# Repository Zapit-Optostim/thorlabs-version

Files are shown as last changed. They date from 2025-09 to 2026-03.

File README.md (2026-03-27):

# zapit-CAD

Zapit is a random-access spatio-temporally precise scanning system for optogenetics experiments. This repo consists of resources on the parts used, CAD models for their construction and instructions for assembly. 

See the [Parts List](Parts_List.md) for a list of parts required for constructing Zapit.

The CAD models show you each part needed (where available) to construct the system and a rendering of how these pieces should be put together. 

The orientation of the parts are not set in stone, and therefore do not have to be set exactly as they are in these models. However,  the 'order' of pieces is very important, and it helps to think about this best in terms of the direction of the light path from the laser (see Fig. 1a in the paper to help with visualisation). Additionally, the distance between parts is dependent on the objective and tube lenses you use for the distance needed from your sample. Please get in touch if you have trouble finding the right combination for your experiments. 

We also have adaptor parts for each laser in the 'Thorlabs-parts' folder to connect the laser to Thorlabs parts, which are the only custom part as part of this system design. These parts have worked for us but you are free to design and machine your own. We recommend getting these adaptor plates CNC milled, rather than 3D printed, as depending on your stimulation protocol, these lasers are prone to overheating, which may turn your laser off automatically within an experiment (such as with the Obis lasers). These parts are also only appropriate if you are using the laser without their corresponding heatsink. If you are using the heatsink, you will have to design your own part to attach both the laser and heatsink. 

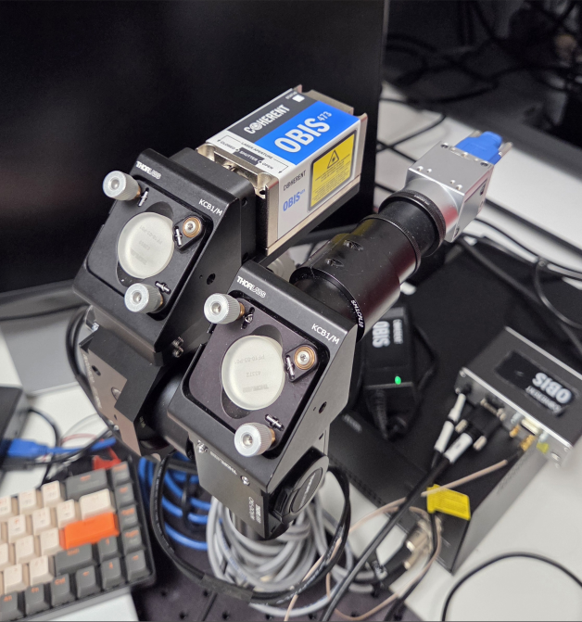
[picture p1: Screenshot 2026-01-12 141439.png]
 

We are keen to help others build the system, so if you feel you lack information please make contact via GitHub and we will get you up and running. 

If you need additional sound-proofing, you can build the custom enclosure, which is found [here](https://github.com/Zapit-Optostim/zapit_CAD)

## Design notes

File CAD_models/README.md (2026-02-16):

The following is a set of assembly instructions for the Thorlabs set up. This is the same for all lasers, the only changes are the laser, adaptor plate and filters needed.

If you want to change the focal distances based on your set up (which depends on how far the mouse is from the lens), the larger of the focal distance lens combinations (see paper, under Hardware design) should be the objective lens to keep the magnification at 0.5x.
You can also change the length of the rods for your needs, and how close you want pieces coupled together.

| Step | Instruction | Visual Aid |
| ---- | ----------- | ---------- |
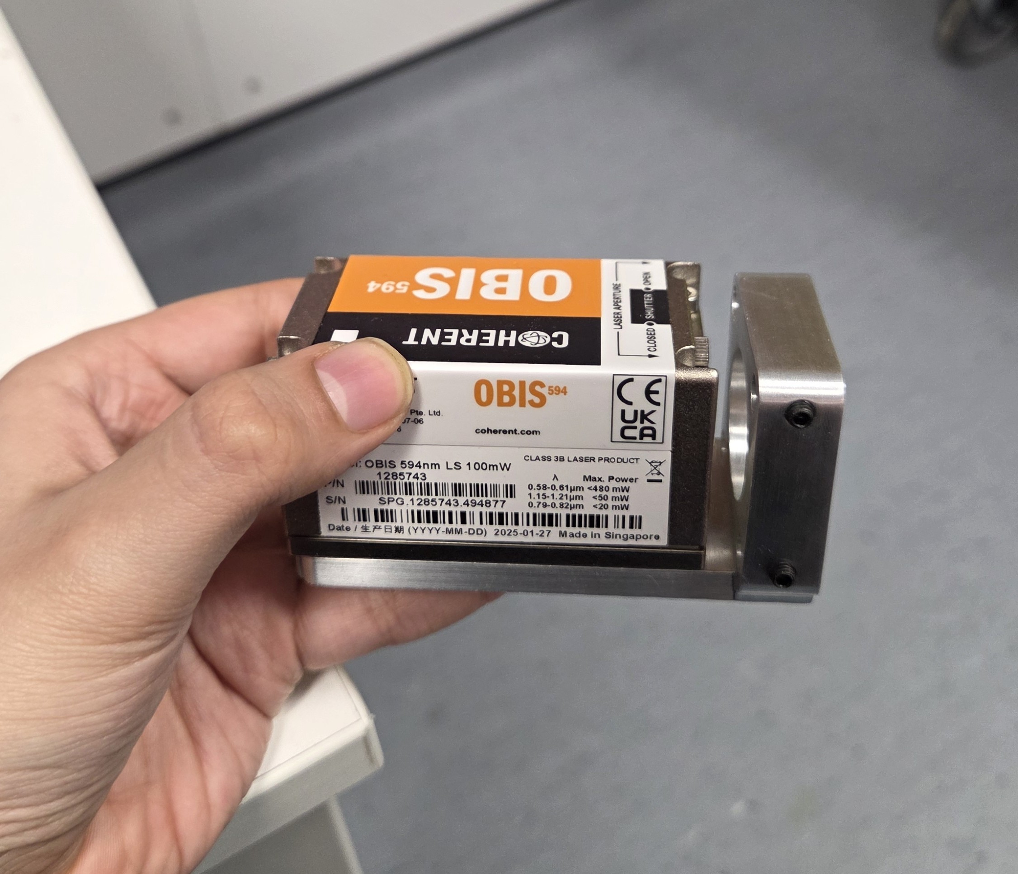
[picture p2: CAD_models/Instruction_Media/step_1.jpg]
Step 1
|   1  | Attach the laser to the adaptor plate with screws (check the hole size in CAD).| |
|  2   | Carefully place a silver mirror (PFR10-03-P01) in a right angled mirror holder (KC1B/M) by loosening the black side screw to make room for the silver mirror insertion (reflective side facing inwards), and then tighten to lock it into place.| Step 2|
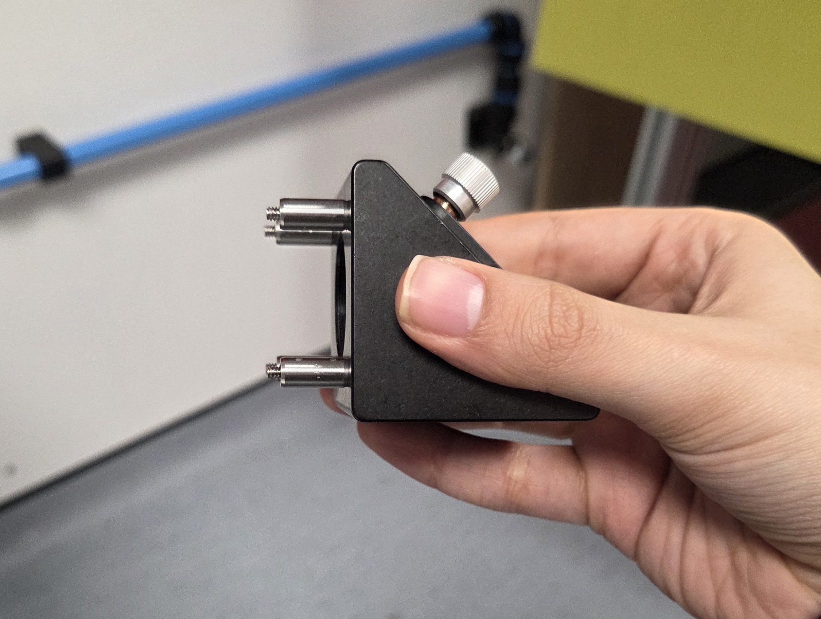
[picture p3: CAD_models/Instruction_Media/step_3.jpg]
Step 3
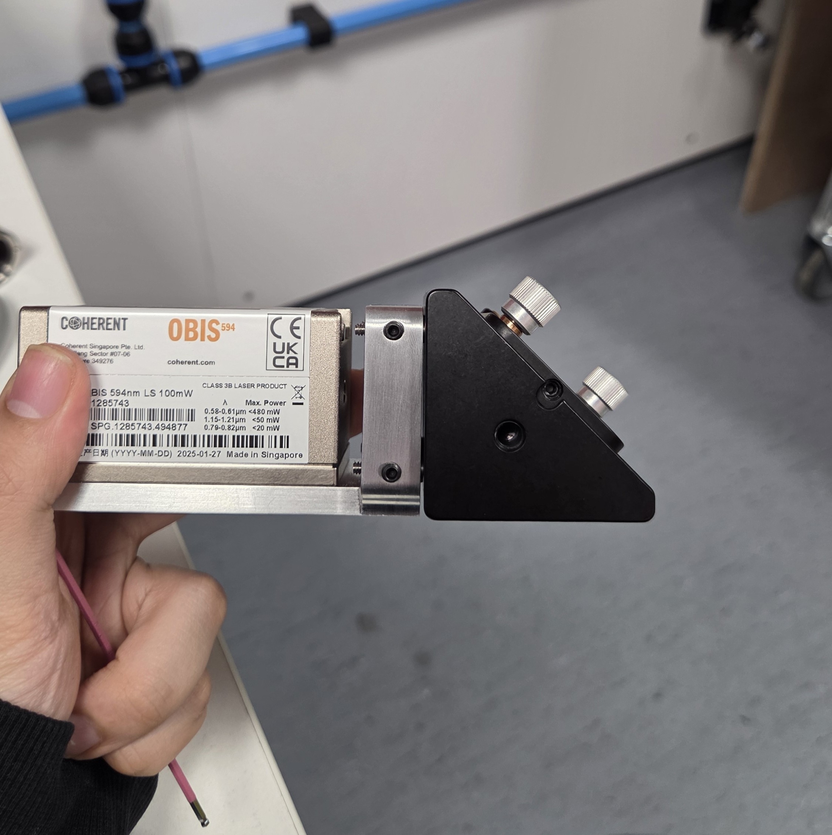
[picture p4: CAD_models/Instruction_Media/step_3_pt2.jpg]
Step 3 Continued
|  3   | Screw in cage rods (ER05) into the same KC1B/M part above in order to connect the laser adapter plate to the right angled mirror holder. Check the side holes in the CAD model to see which size screws you need for securing the ER rods into the custom adaptor plate.|  |
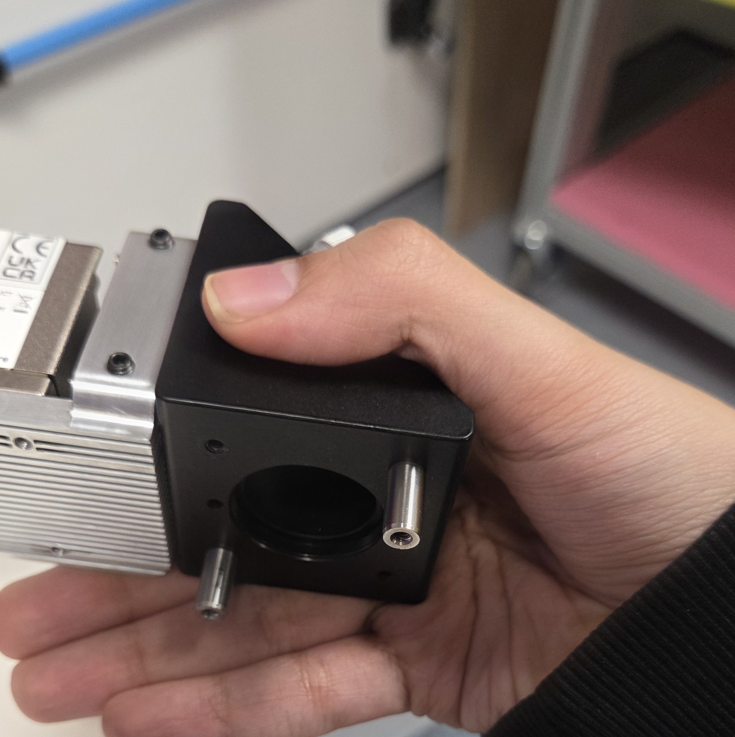
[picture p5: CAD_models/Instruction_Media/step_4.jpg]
Step 4
|  4   | Screw in ER05 rods into the other side of the KC1B/M part.| |
|  5   | Attach a lens tube (SM1L03) to couplers (SM1T010) on one side.| Step 5|
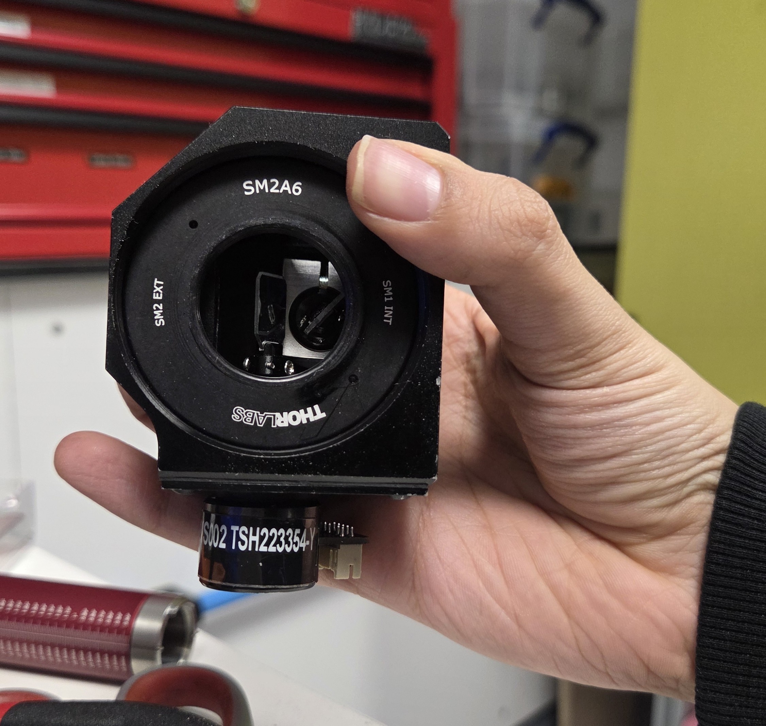
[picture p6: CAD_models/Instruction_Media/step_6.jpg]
Step 6
|  6   | Screw in one side of the lens tube into the threading ring (SM2A6) screwed into the large end of the galvos.| |
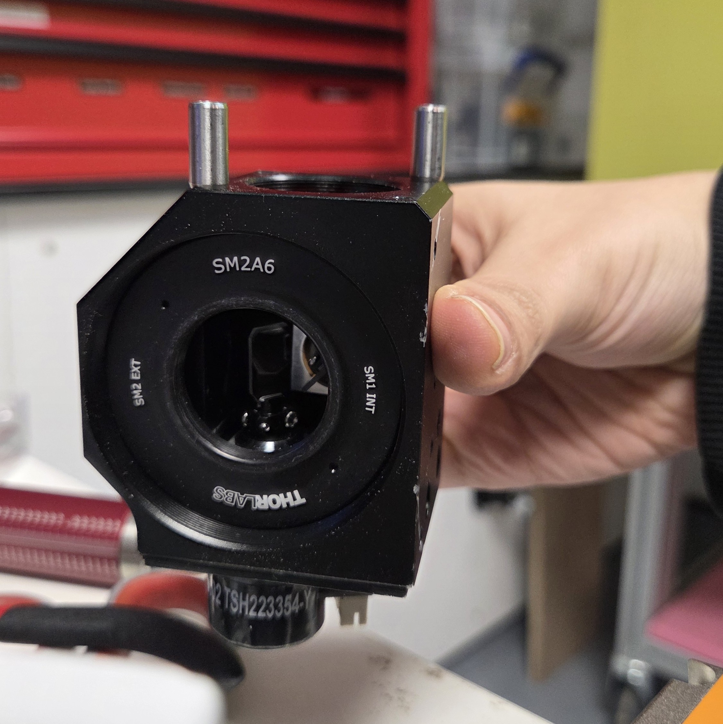
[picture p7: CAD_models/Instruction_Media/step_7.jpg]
Step 7
|  7   | Screw in ER05 rods into the galvo housing.| |
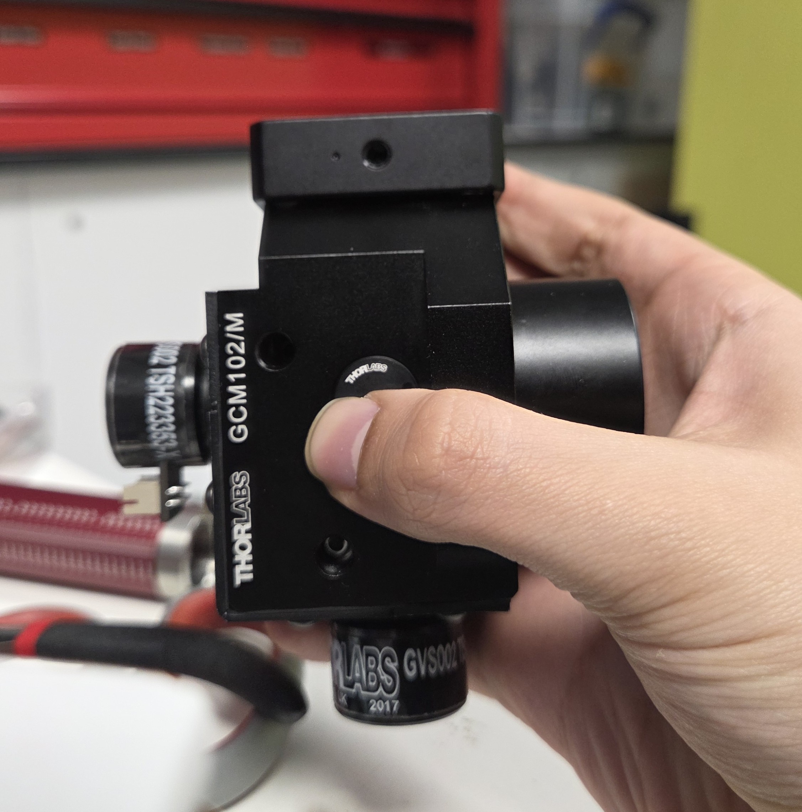
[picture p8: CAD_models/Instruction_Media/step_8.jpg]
Step 8
|  8   | Connect the KC1B/M and the galvo housing with a cage plate inserting the rods in the holes of the cage plate (CP33T/M), and tighten the rods into place with the side screws.| |
|  9   | Insert your dichroic filter into the cage cube (CM1-DCH/M). There are small black screws to take out the base of the cage cube that has pinchable parts which move the clamp for the mirrors outwards. Gently place the dichroic filter in the correct orientation (the one that reflects more light should end up facing the galvos) after pinching to make room for the mirror, and release after properly placed. Screw the base plate back into the rest of the cage cube.| Step 9 Step 9 Continued|
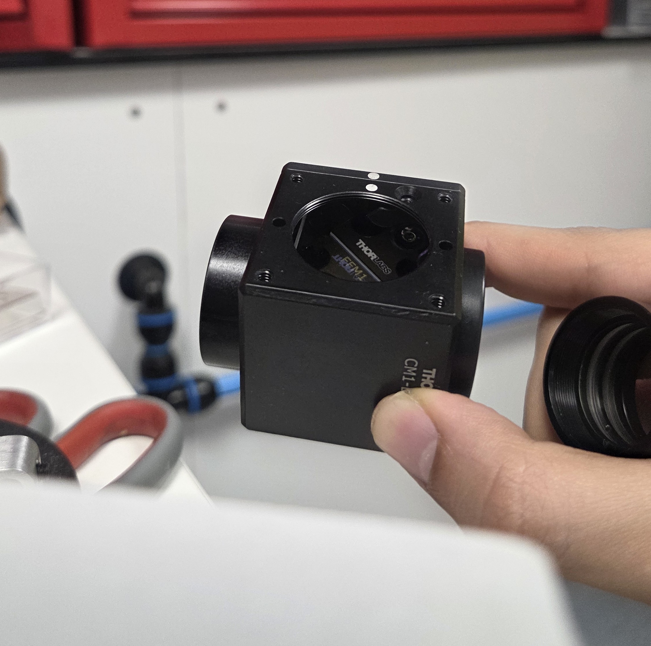
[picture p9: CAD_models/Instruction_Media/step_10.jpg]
Step 10
|  10  | Attach another lens tube (SM1L03) into the side of the cage cube where the reflective part would face the galvos. Snap on a cap (SM1EC2B) on the other side of the cage cube to prevent light escaping.| |
|  11  | Take a lens tube (SM1L10), and remove one threading ring with an SM1 lens tool. Insert two lens (the set with the larger focal distance) carefully with the SM1 lens tube, with the convex (curved) sides of each lens touching each other. The depth at which the lens should be depends on the lens combination used and the distance this should be from the tube lens, which is all ultimately dependent on the distance the setup will be from your mouse. Put the threading ring back in.| Step 11|
|  10  | Attach another lens tube (SM1L03) into the side of the cage cube where the reflective part would face the galvos. Snap on a cap (SM1EC2B) on the other side of the cage cube to prevent light escaping.| Step 10|
|  11  | Take a lens tube (SM1L10), and remove one threading ring with an SM1 lens tool. Insert two lens (the set with the larger focal distance) carefully with the SM1 lens tube, with the convex (curved) sides of each lens touching each other. The depth at which the lens should be depends on the lens combination used and the distance this should be from the tube lens. Put the threading ring back in.|            |
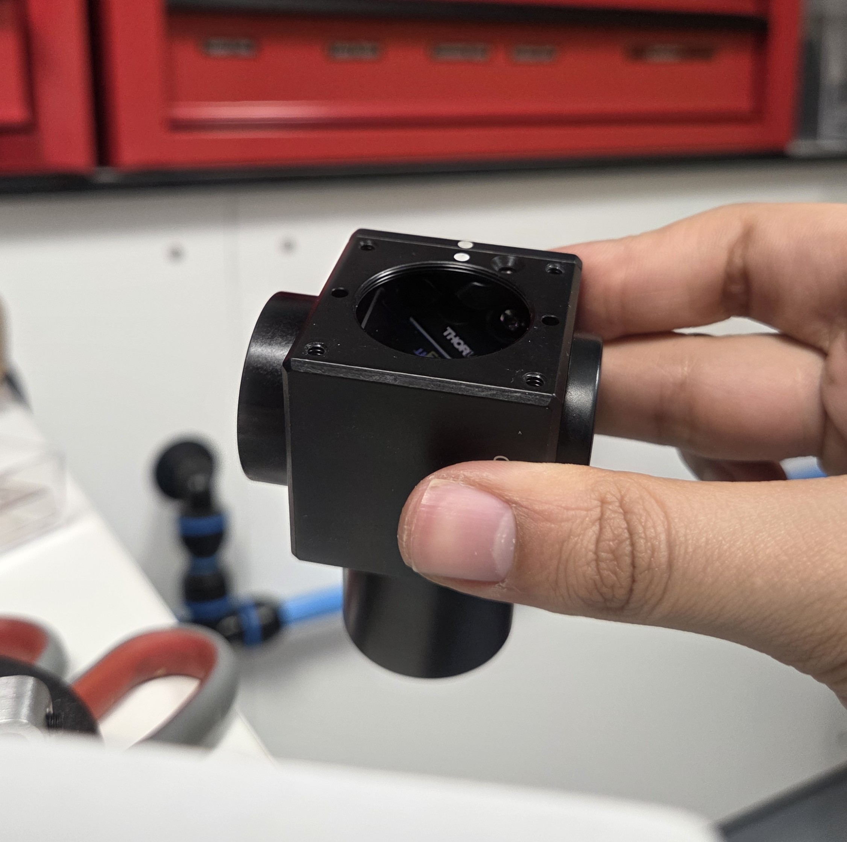
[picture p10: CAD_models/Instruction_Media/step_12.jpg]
Step 12
|  12  | Screw in the lens tube (SM1L10) to the side of the cage cube where the light would be redirected to (i.e.:the light reflects off the dichroic filter and goes downwards at a 90 degree angle).| |
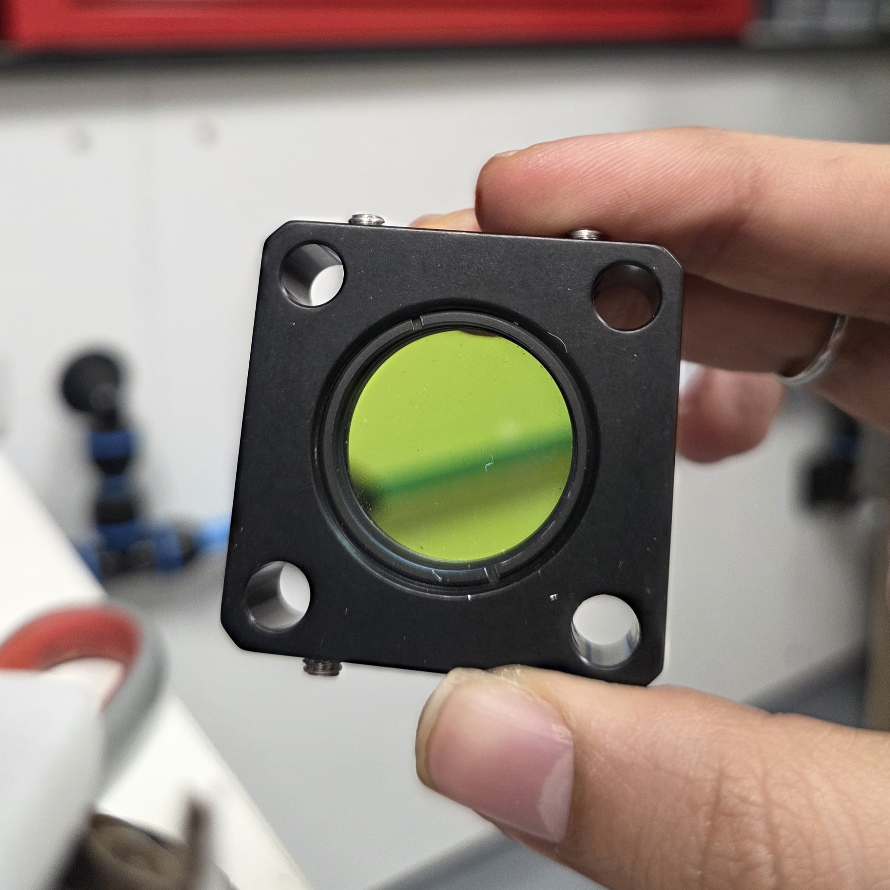
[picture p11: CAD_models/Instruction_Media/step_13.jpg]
Step 13
|  13  | Remove the threading ring of a cage plate (CP33T/M) and put in the emission filter with the more reflective side facing the dichroic filter (i.e.: faces down, towards the incoming light). | |
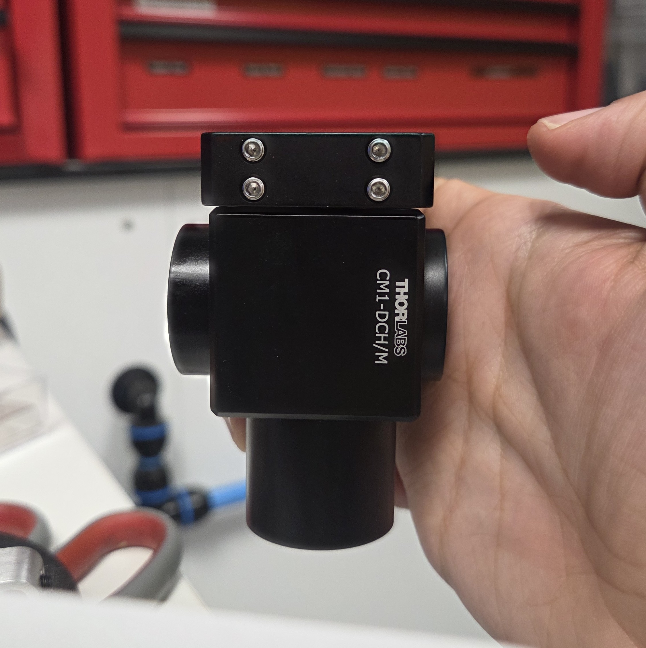
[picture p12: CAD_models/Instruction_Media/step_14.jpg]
Step 14
|  14  | Screw in ER025 rods into the top of the cage cube with the dichroic and then secure this cage plate, with the filter facing downwards. | |
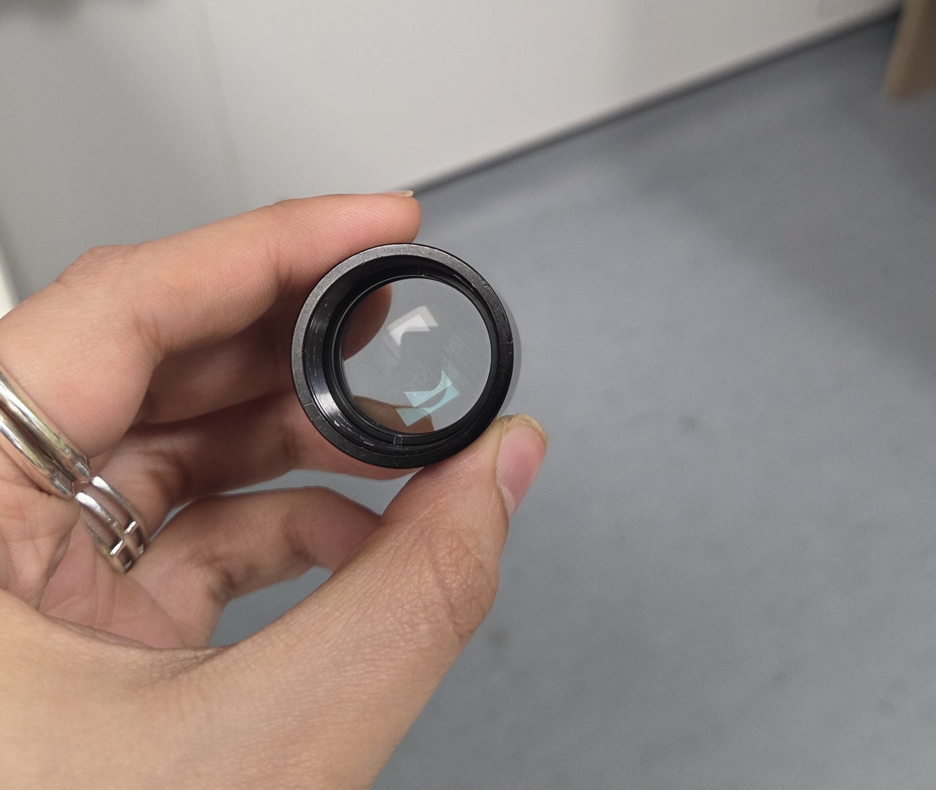
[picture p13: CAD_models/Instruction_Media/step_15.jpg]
Step 15
|  15  | Insert the two lenses for the tube lens into another SM1L1O. | |
|  16  | Screw this tube lens into one side of the cage cube mounted silver mirror (CCM1-P01/M). | Step 16|
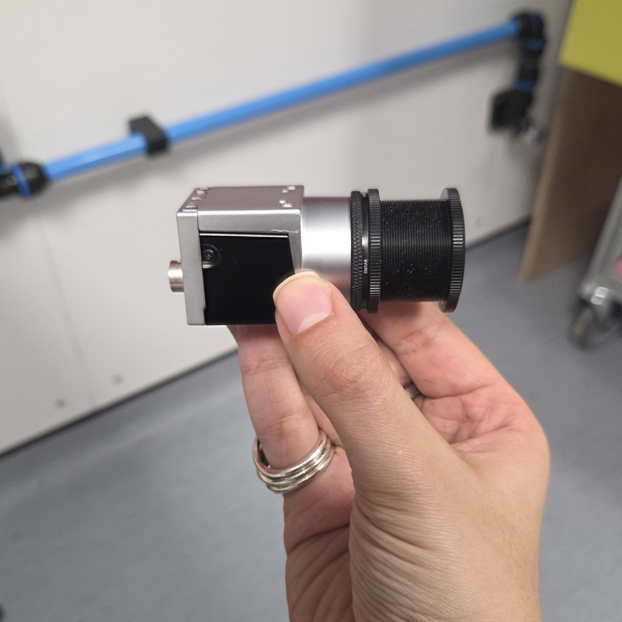
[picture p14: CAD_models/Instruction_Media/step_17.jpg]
Step 17
|  17  | Screw in a C-mount coupler (SM1A9) and SM1 coupler (SM1T1O) to the Basler camera. | |
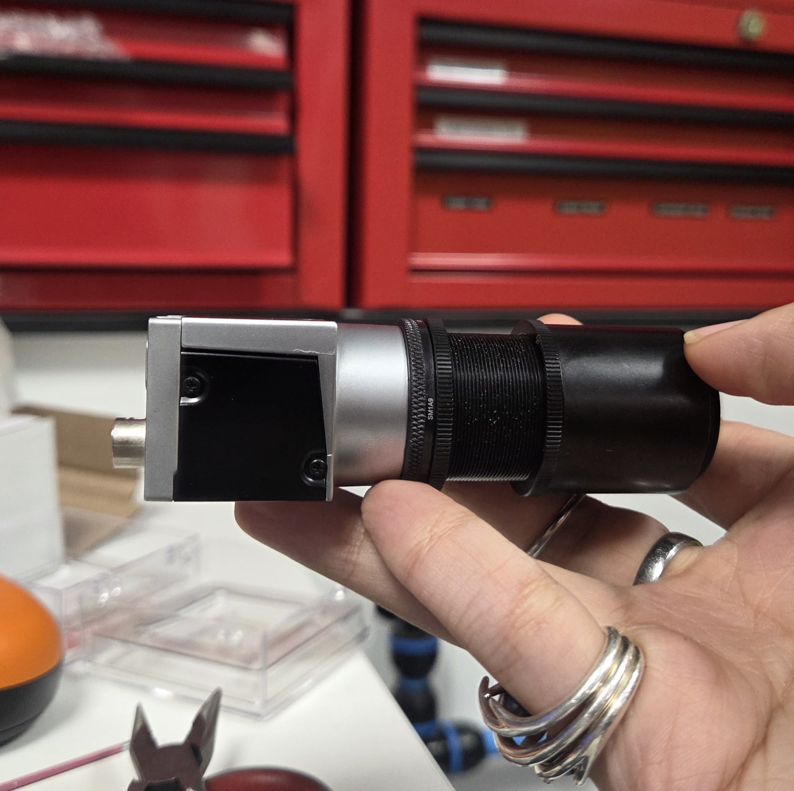
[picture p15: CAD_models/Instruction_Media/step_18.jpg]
Step 18
|  18  | Screw in a lens tube (SM1L05) to the coupler. | |
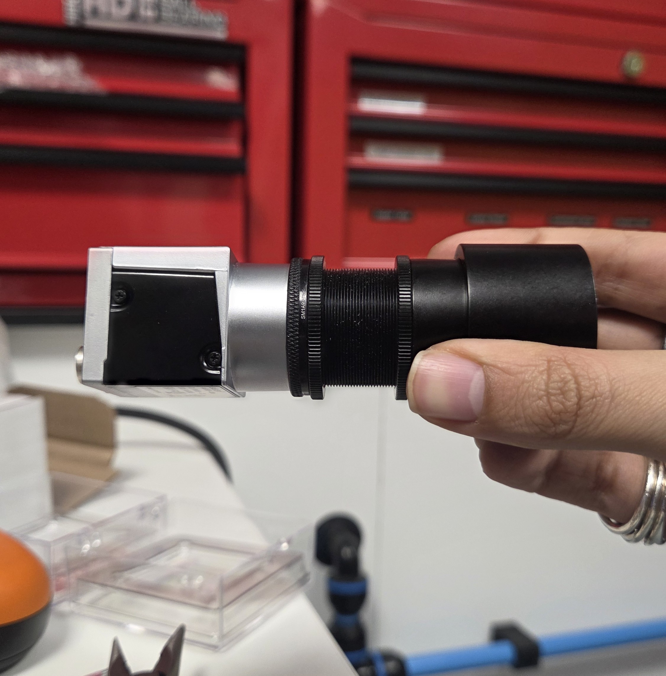
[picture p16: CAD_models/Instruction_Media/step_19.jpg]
Step 19
|  19  | Screw in a coupler (SM1CPL10) to the lens tube. | |
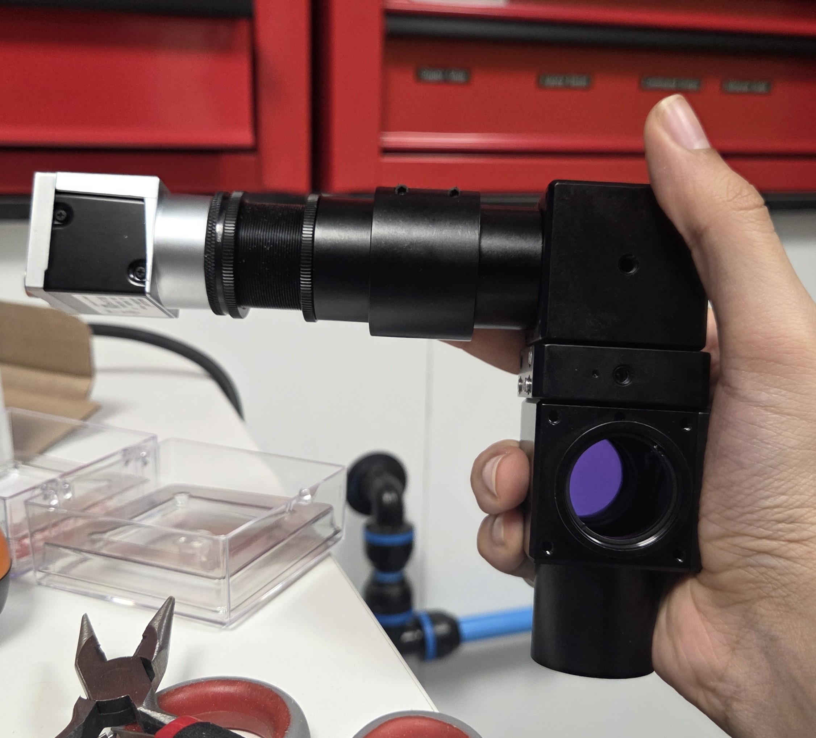
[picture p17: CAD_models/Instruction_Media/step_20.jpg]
Step 20
|  20  | Connect the CCM1-P01/M with the tube lens to the other side of the coupler, and then connect ER025 rods to the other side of the CCM1-P01/M to secure the rest in place by the cage plate holding the emission filter. | |
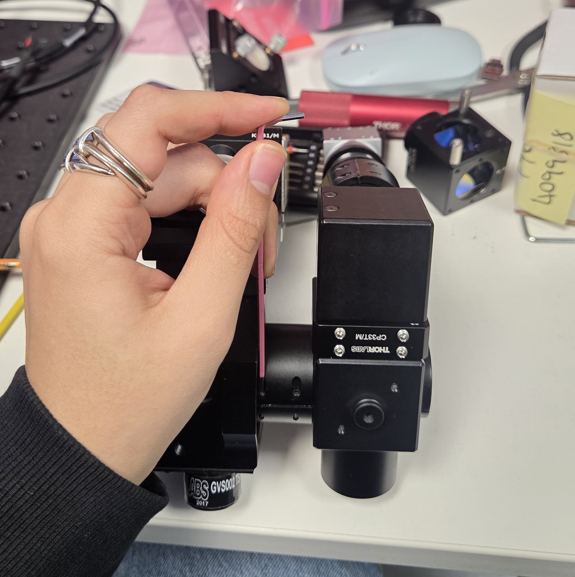
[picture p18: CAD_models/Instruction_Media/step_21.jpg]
Step 21
|  21  | Connect the exposed end of the cage cube holding the dichroic to the galvos via another SM1T10 coupler. | |
|  22  | Mount to your set-up as desired.| Step 22|

Please get in touch if anything is unclear or you have an issue!

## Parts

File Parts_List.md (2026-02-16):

# Parts list

Prices are correct as of September 2025.
Metric part numbers are listed but Imperial are also available (remove the `/M` from the ThorLabs product codes).

## 1. Common optomechanical parts
Regardless of how you assemble the components, you will require the following.
| Item | Description | Approx Cost |
| --- | --- | --- |
| [MF252-39](https://www.thorlabs.com/thorproduct.cfm?partnumber=MF525-39) OR [Chroma AT495LP](https://www.chroma.com/products/parts/at495lp) | 25 mm emission filter | 200 GBP |
| [MD498](https://www.thorlabs.com/thorproduct.cfm?partnumber=MD498) | GFP dichroic  (see below)| 200 GBP |
| 2x [AC254-200-A](https://www.thorlabs.com/thorproduct.cfm?partnumber=AC254-200-A) | f=100 mm achromatic lens (objective) | 65 GBP |
| 2x [AC254-100-A](https://www.thorlabs.com/thorproduct.cfm?partnumber=AC254-100-A) OR 2x [AC254-150-A](https://www.thorlabs.com/thorproduct.cfm?partnumber=AC254-150-A) | f=50/f=75 mm achromatic lens (tube lens) | 65 GBP |
| [SM1A9](https://www.thorlabs.com/thorproduct.cfm?partnumber=SM1A9) | C-Mount to SM1 adapter | 16 GBP |

* You need an emission filter before the camera to block direct laser light.
You can either use something like a GFP filter or a low pass filter.
Two options are listed above.
The low-pass filter will work better in dimmer environments. 

* For lasers of different wavelengths, we have different options. 
 - For example, we have used a ZT473_594rpc-UF dichroic from Chroma (custom ordered | 428.32GBP) and [zet488-594nm](https://www.chroma.com/products/parts/zet488-594m) (518.48) emission filter for our 594nm laser. This dichroic and emission filter works with our 450nm laser too. 
 - It is worth noting, filters will be cheaper for single-band transmission

* With Basler a acA1920-40um camera the FOV of a system built with a f=100 mm objective and f=75 mm tube lens will be about 13.5 mm by 9.5 mm. 
This should yield about 7.8 microns/pixel.
Switching to an f=50 mm tube lens gives about 22 mm by 14 mm. Should yield about 11.72 microns/pixel.
The shorter tube lens is recommended to get the whole mouse skull into the FoV at once, but YMMV if you choose a different camera. 

**NOTE:** You will also need parts to mount the enclosure within your rig.
These are not included above.
If you need to add focusing ability you can buy ThorLabs [PT1/M](https://www.thorlabs.com/thorproduct.cfm?partnumber=PT1/M).
Alternatively, you might focus by moving the sample up and down. 

## 2. Optomechanical parts for the main set-up
If you are building the Thorlabs-compatible version with no enclosure, you will need the following parts:

| Item | Description | Approx Cost |
| --- | --- | --- |
| 1x [CM1-DCH/M](https://www.thorlabs.com/thorproduct.cfm?partnumber=CM1-DCH/M) | Cage cube to hold dichroic filter| 14 GBP |
| 8x [ER025](https://www.thorlabs.com/thorproduct.cfm?partnumber=ER025) | 1/4" cage rods for connecting multiple parts, such as laser adapter to right angled mirror | 32 GBP |
| 1x [PFR10-03-P01](https://www.thorlabs.com/thorproduct.cfm?partnumber=PF10-03-P01) | Ø1" Protected Silver Mirror | 48 GBP |
| 1x [SM1L05](https://www.thorlabs.com/thorproduct.cfm?partnumber=SM1L05) | 0.5" SM1 lens tubes to house tube lens | 12 GBP |
| 1x [SM1L10](https://www.thorlabs.com/thorproduct.cfm?partnumber=SM1L10) | 1" SM1 lens tubes to house objective lens | 13 GBP |
| 2x [SM05L03](https://www.thorlabs.com/thorproduct.cfm?partnumber=SM05L03) | 0.3" SM05 lens tube to couple to adapter connecting cage cube and scanners | 12 GBP | 
|2x [SM1CPL10](https://www.thorlabs.com/thorproduct.cfm?partnumber=SM1CPL10) | To couple the camera to its lens tubes, and the scannerto its lens tubes | 70 GBP |
| [SM2A6](https://www.thorlabs.com/thorproduct.cfm?partnumber=SM2A6) | SM2A6 Threading ring to insert into scanners and to join with 1X SM1CPL10  | 25 GBP |
| [SM1EC2B](https://www.thorlabs.com/thorproduct.cfm?partnumber=SM1EC2B) | Snap on cap to block light exiting the cage cube | 10 GBP |
| 2x [CP33T/M](https://www.thorlabs.com/thorproduct.cfm?partnumber=CP33T/M) | SM1-Threaded Cage plates to house emission filter and connect galvos to a right-angled mirror mount | 45 GBP |
| 1x [KCB1/M](https://www.thorlabs.com/thorproduct.cfm?partnumber=kcb1/M) | Right-angled mirror mount to hold silver mirror which direct laser light | 132 GBP |
| 1x [CCM1-P01/M](https://www.thorlabs.com/item/CCM1-P01_M) | Camera fold mirror with cage cube | 150 GBP |

We also used a translation stage for focusing and mounting, which are coupled to our scanners, by using a custom designed, 3D-printed plate. This does not have to be CNC machined, but you may prefer to do so for your set-up. 

## 3. Mounting the laser in the general set-up
For mounting the laser, we have chosen to go without the heatsinks but have designed custom adapters to join onto our Thorlabs set-ups. For the Obis laser, we have implemented a heat-sink like design as it is possible for it to shut off if it reaches temperatures above 40 degrees Celsius. All custom adapters are available in our CAD models of our set-ups, as well as individual files. We recommend getting these created by a CNC machining service, we used [HLH](https://www.hlhprototypes.com/cnc-machining/) as they are budget-friendly. For example, our Oxxius adapter was about 60 GBP and Obis adapter plate was about 120 GBP (both excluding shipping). 

These adapter plates were designed with Thorlabs parts in mind, so you should be able to use 1/2" ER posts (included above), M4 locking set screws for the Oxxius plate, and assorted screws that come with the Obis laser for the Obis plate. 

## 4. The expensive parts
All systems will require the following.

### USB Camera
We have been using the [Basler ace acA1920-40um Monochrome USB 3.0 Camera](https://www.edmundoptics.co.uk/p/basler-ace-aca1920-40um-monochrome-usb-30-camera/3421/) which retails at about 550 GBP.
This camera works well.
The sensor is about 11 by 7 mm and our hardware magnifies by a factor of 0.5 so the whole sample is visible.
In principle cameras by other manufacturers will also work, but this is not currently supported by the software.
Adding support is not planned at present, but would involve adding seperate classes for each camera type and modifying the settings system to cope with this. 
It is easier to buy the Basler camera.

### DAQ
The software requires an NI DAQ with four analog output channels.
The existing stimulators in the experiments are currently using an NI USB-6363, which is acceptable in terms of performance and easy to work with.
We have also tested all lasers with a USB-6453, and has been more useful with an analog input section for testing, larger bandwidth on the bus (USB 3) and a bigger FIFO buffer.

This device comes in different formats:
* Model 782259-01 requires two BNC-2090A breakout boxes and associated cables. 3100 GBP
* Model 781443-01 is screw terminal based and so won't require breakout boxes. 3250 GBP
* Model 782258-01 has an integrated breakout box, which is easier to work with than screw terminals, but more expensive. 3800 GBP.
* Model  782257-01 is an OEM board that can potentially be integrated into a custom enclosure along with the scanner control board and associated PSUs.

Finally, there is the *possibility* that a PCIe-based device might perform a little better during the stimulus ramp down.
If you have a spare PCIe slot and do not care about the possibility of making an intergrated enclosure for all the electronics, you can buy a PCIe-6363 (781051-01, 2300 GBP) plus two BNC-2090A breakout boxes and associated cables.

### Laser
So far we have worked exclusively with the [473 nm Obis laser 75 mW](https://coherentinc.force.com/Coherent/1185052?cclcl=en_US).
These units are are quite expensive at 6000 GBP.
We have bought the free space version and directly fed it into the scan head. 
We have not tried fibre-coupling for this application.
The output of 75 mW is more than enough for 2 points with a duty cycle of 50% and can do up to about 20 points with a time-averaged power of 2 mW and good mirror coatings. 
We are using the Obis lasers because they have proven to be reliable, stable, and switch very quickly.

The Obis laser will need one [male SMB to male BNC cable](https://uk.rs-online.com/web/p/coaxial-cable/7600405) to interface with the DAQ. 

We have also tested 
* [Oxxius 450 nm 100 mW](https://www.oxxius.com/products/lbx-405-5/) at about 3100 GBP 
* [Obis 594 nm 100Mw](https://coherentinc.my.site.com/Coherent/lasers/lasers-laser-systems/obis-lx-ls/1285744?cclcl=en_UK) at about 9400 GBP.

Other (untested) options that are slightly different wavelength but much cheaper and in principle should work well include:
* [Oxxius 450 nm 70 mW](https://www.oxxius.com/products/lbx-405-5/) at about 2800 GBP.
* [Oxxius 488 nm](https://www.oxxius.com/products/lbx-488/) With the 40 mW at about 2800 GBP and the 100 mW at about 6400 GBP.
* [Omicron 633 nm 100mW](https://photonlines.co.uk/product/omicron-luxx-compact-laser-diode/) at about 3200 GBP.

All the laser really needs is the ability to control power with an analog input and a linear power/control input response. Bandwidth of about 200,000 kHz or above should be enough. 
Other companies to consider include [Toptica](https://www.toptica.com/products/single-mode-diode-lasers) and [RPMC Lasers](https://www.rpmclasers.com/product/lbx-488-xxx-csb/). 
YMMV, though, and they are reasonably priced so might be worth a look.

### Scanners
We use [ThorLabs GVS002](https://www.thorlabs.com/thorproduct.cfm?partnumber=GVSK2-EC), which are cheap and easy to mount. These scanners have a lower bandwidth than the Saturn scanners and can cope with up to 5 points in a trial, depending on their spacing. These scanners have been tested with all lasers in the manuscript but have not been used experimentally so far. 

The scanners used in the custom enclosure and in the experiments in the paper are the [5 mm Saturn Scanners](https://www.edmundoptics.co.uk/p/5mm-aperture-protected-silver-saturn-5b-dual-axis-galvanometer-scanner/44527/), which are generally kept in stock by Edmund and retail for 2900 GBP.
They perform very well are near silent under the conditions that we run them.
Avoid Cambridge Technologies: their lead times are around 1 year and you will need to buy a spare set to insure yourself against potential down time should the scanners fail.
Failures happen and even repairs under warranty can take many months from this vendor.

The scanners come with a controller card but you will also need to buy two PSUs (to generate the +/- 24 V needed).
We are using [Mean Well Switching Power Supply, 24V dc, 4.2A](https://uk.rs-online.com/web/p/switching-power-supplies/8157450), which retail at about 65 GBP each.

Please note these power supplies have exposed screw terminals carrying mains voltage.
Talk to an experienced engineer if you are unsure about wiring and housing them safely.

## 5. Tools and small parts
The following is a list of small parts and tools needed to build the system.

* Hex keys: 1.5 mm, 2.5 mm, 3/32, 0.05"
* 3x 3 mm grub screws. 5 mm long are fine too
* [SM1 lens tool](https://www.thorlabs.com/thorproduct.cfm?partnumber=SPW602)

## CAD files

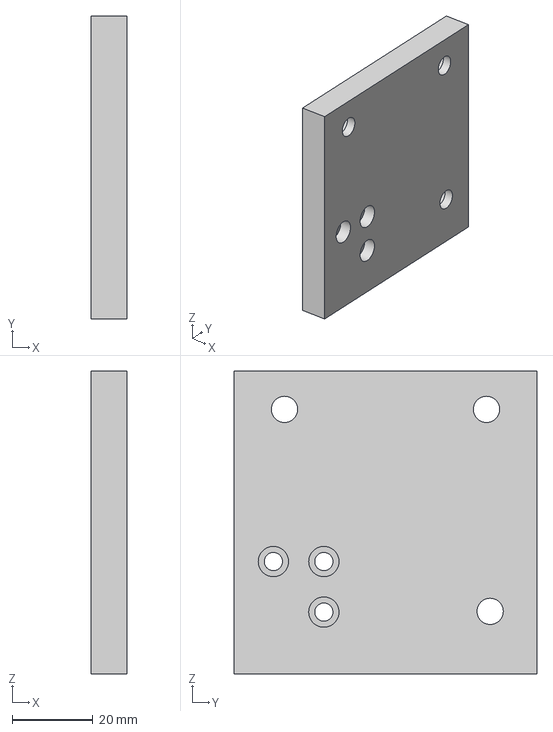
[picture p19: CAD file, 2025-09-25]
CAD_models/TranslationStage_Adapter.step
9.00 x 75.0 x 75.0 mm

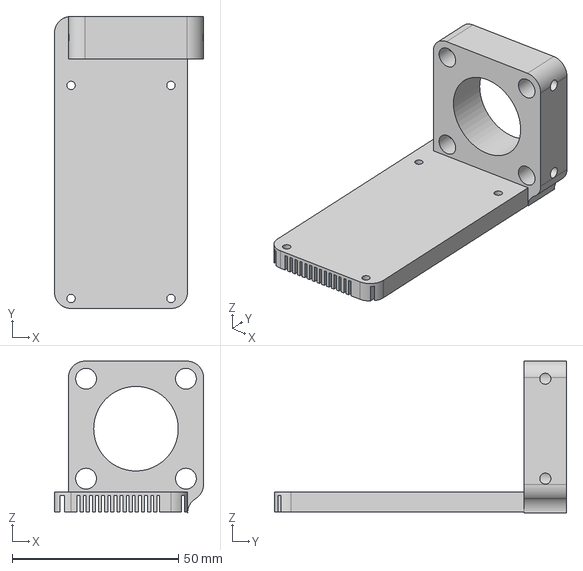
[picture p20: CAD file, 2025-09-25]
CAD_models/Obis_Thorlabs/Obis_adapter_plate.step
44.8 x 87.7 x 45.6 mm

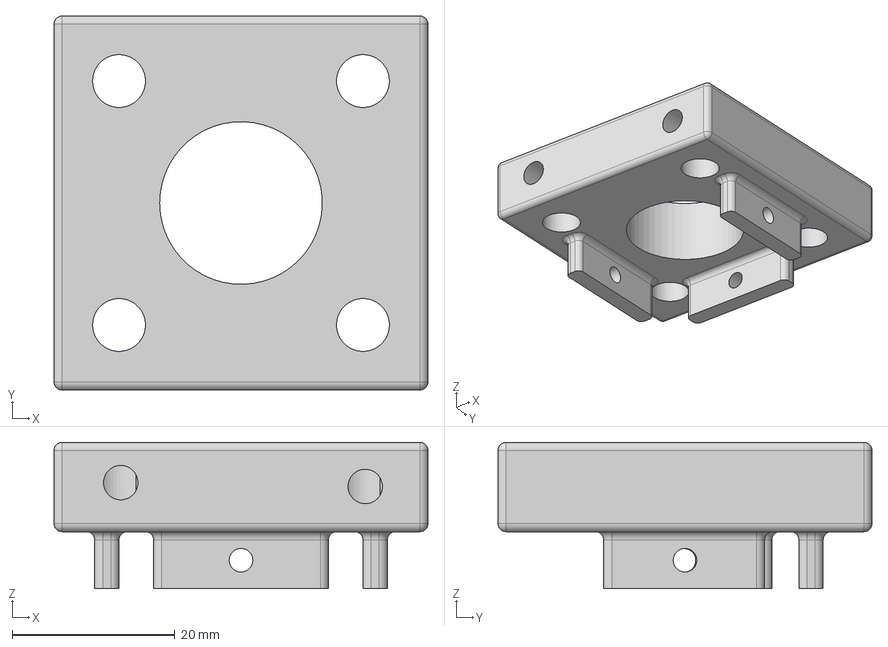
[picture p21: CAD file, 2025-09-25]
CAD_models/Oxxius_Thorlabs/Oxxius_adapter_plate.step
46.0 x 46.0 x 18.0 mm

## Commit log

2024-10-18 remove incompatible lasers
2025-09-25 initial thorlabs version commit
    [Obis_adapter_plate.step, Oxxius_adapter_plate.step, TranslationStage_Adapter.step]
2026-01-12 Add README for CAD models and assembly options
2026-01-12 Clarify assembly instructions and adaptor part details
2026-01-12 Add assembly instructions for Thorlabs setup
2026-01-12 Revise assembly instructions for Thorlabs setup
2026-02-04 Rename Complete Setup_Obis.step to CompleteSetup_Obis.step
    [CompleteSetup_Obis.step]
2026-02-04 Rename Complete Setup_Oxxius.step to CompleteSetup_Oxxius.step
    [CompleteSetup_Oxxius.step]
2026-02-16 testing instructions, removed custom enclosure
2026-02-16 Fix lens tube part numbers in README
2026-02-17 Correct lens tube model in step 15 of README
2026-02-17 removing all mention of custom wherever found, also changing folder structure
    [Obis_adapter_plate.step, Oxxius_adapter_plate.step, TranslationStage_Adapter.step]
